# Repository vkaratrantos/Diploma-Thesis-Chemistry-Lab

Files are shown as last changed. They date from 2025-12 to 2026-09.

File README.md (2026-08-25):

# Automated Chemical Synthesis with a 7-DOF Robotic Arm

Diploma thesis — Electrical and Computer Engineering, University of Patras.
Division of Systems, Control and Robotics.

A robotic system that automates liquid-handling in a chemistry lab: it locates
test tubes visually, picks them up, carries them to a mixing vessel and pours,
keeping the tube upright throughout so nothing spills.

The system does not work from taught positions. Tube and vessel locations
come from ArUco markers detected at runtime, so the rack can be moved between
runs and the arm adapts.

---

## The problem

Three problems that a simple pick-and-place demo does not have:

1. The tube must stay upright.
2. Positions are not known in advance.
3. A 7-DOF arm is redundant.

---

## Hardware

| | |
| --- | --- |
| Arm | Elephant Robotics MyArm 300 Pi (7 DOF) |
| Gripper | Custom, Thorgripper |
| Camera | Creative Livecam HD |
| Markers | ArUco, 30 mm |
| Compute | Raspberry Pi on the arm + external PC for planning |

---

## How it works

```
camera ──► ArUco detection ──► TF frames (marker_1 … marker_6)
                                     │
                                     ▼
                       planning scene (tubes + mixing vessel)
                                     │
                                     ▼
                           MoveIt 2 ──► trajectory
                                     │
                                     ▼
                                MyArm 300 Pi
```

**Vision.** ArUco markers on the rack and the mixing vessel are detected and
published as TF frames.
Camera-to-arm calibration in aruco/calibrate_camera.py .

**Planning.** Approaches are planned backwards: IK solution found at the
grasp pose first, and the standoff above it is seeded from that solution, so
both ends share an IK branch. Each candidate standoff is then verified by
dry-running the actual descent from it before the arm commits to moving there.

**Keeping the tube upright.** Rather than asking OMPL to respect an orientation
constraint in the full 7-DOF space, transits search the 5-DOF manifold on which
the constraint is already satisfied — joints 1–4 plus the roll about the
vertical, with the wrist recovered in closed form.

---

## Repository layout

| Path | What it is |
| --- | --- |
| [`aruco/aruco_anchor.py`](aruco) | Marker detection, TF publishing |
| [`aruco/calibrate_camera.py`](camera_calibration) | Intrinsics and camera-to-arm calibration |
| [`robot_initialisation/`](MyArm%20300%20Pi) | Arm driver and hardware bridge |
| [`robot_initialisation/`](robot_initialisation) | Startup and homing |
| [`launch/`](launch) | Launch files — fake robot, Gazebo, real arm |
| [`config/`](config) | Kinematics, joint limits, OMPL settings |
| [`GUI/`](GUI) | Tkinter operator interface |
| [`3d_prints/`](3d_prints) | Custom bases and flange (STL files) |
| `simple_move.cpp` | Motion node |

---

## Running

Built and tested on **Ubuntu 22.04 / ROS 2 Humble**, with MoveIt 2 and
MoveIt Task Constructor built from source.

Three modes: fake robot (no hardware), Gazebo, and the real
arm.

### Commands

The GUI publishes on `/gui_commands`
| Command | Action |
| --- | --- |
| `TASK <1-5>` | Full pipeline for each tube |
| `m<0-6>` | Manual move to a marker |
| `o` / `c` | Open / close gripper |
| `p` | Pour |
| `h` | Return home |

## Related

The final packaged ROS 2 workspace is in
[**thesis-repo**](https://github.com/vkaratrantos/thesis-repo)

## Status

Thesis defence scheduled for September 2026. The system runs on the physical
arm; known limitations are documented in the workspace README.

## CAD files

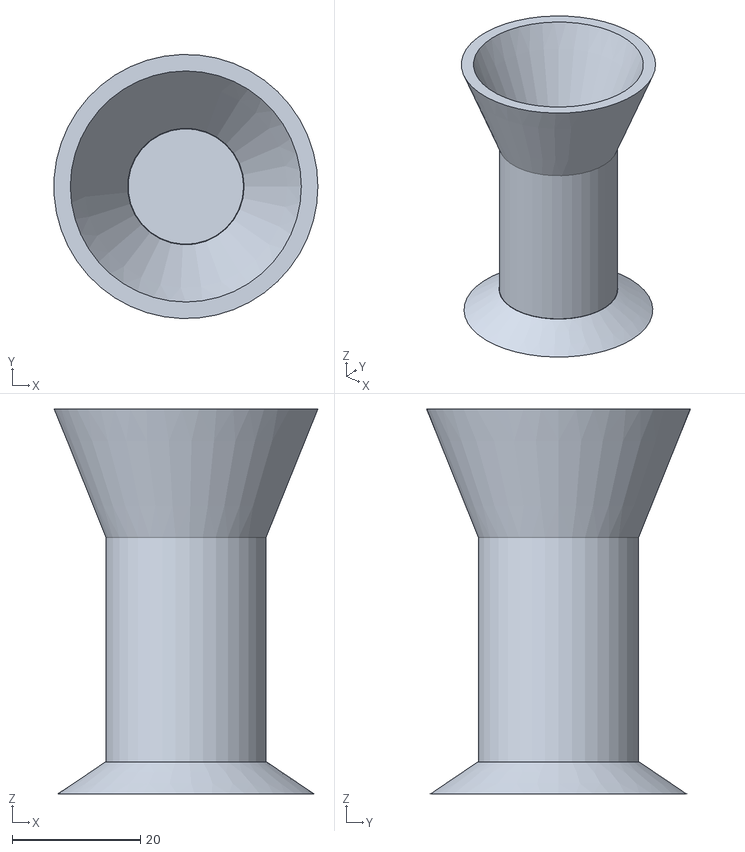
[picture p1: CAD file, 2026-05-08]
3d_prints/bracket_cone.stl
41.1 x 41.1 x 60.0

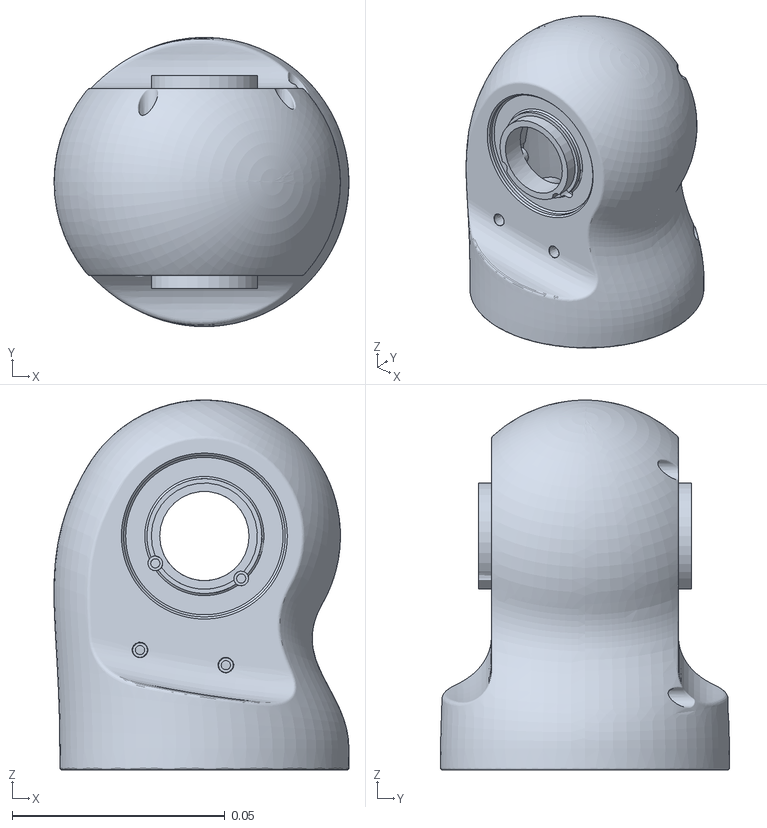
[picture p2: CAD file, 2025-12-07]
MyArm 300 Pi/URDF/j3.stl
0.0694 x 0.068 x 0.087

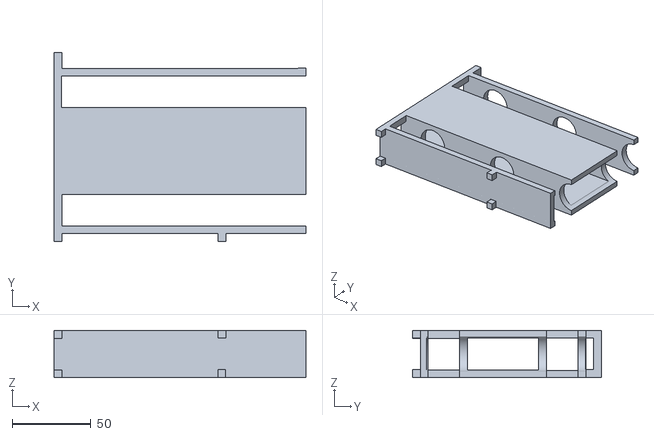
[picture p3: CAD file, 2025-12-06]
3d_prints/rack.stl
160.0 x 120.0 x 30.0

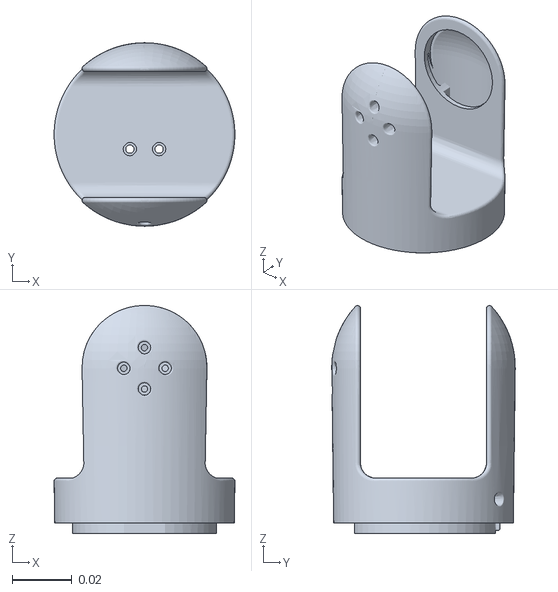
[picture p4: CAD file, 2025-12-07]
MyArm 300 Pi/URDF/j5.stl
0.0603 x 0.0613 x 0.0761

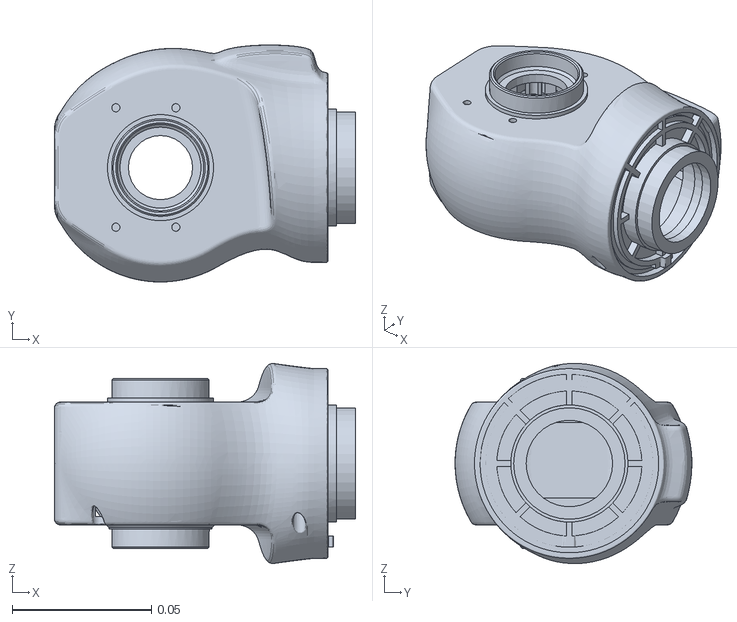
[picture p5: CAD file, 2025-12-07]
MyArm 300 Pi/URDF/j2.stl
0.108 x 0.0849 x 0.0718

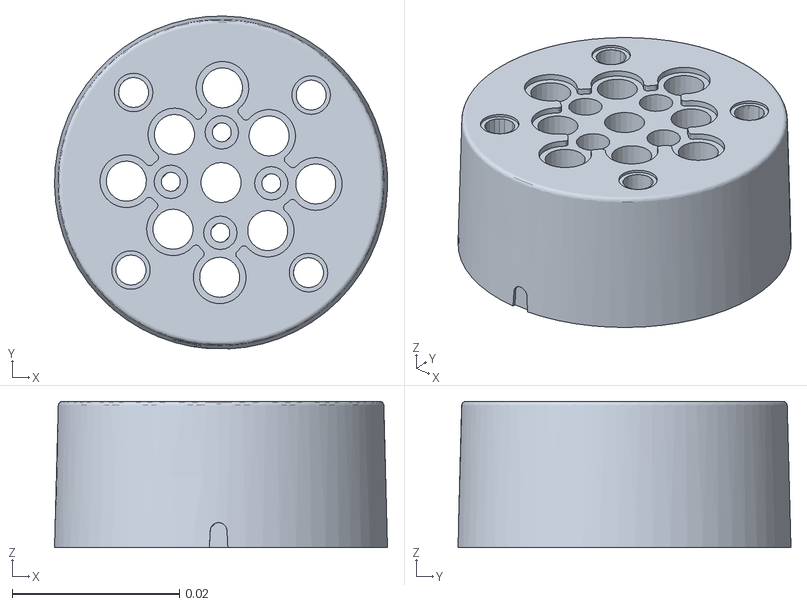
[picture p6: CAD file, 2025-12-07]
MyArm 300 Pi/URDF/j7.stl
0.0398 x 0.0398 x 0.0175

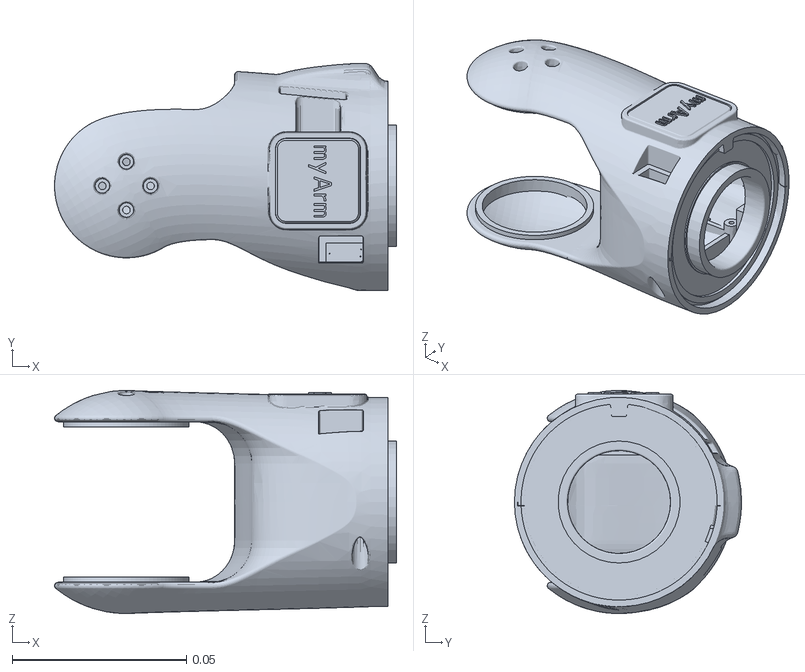
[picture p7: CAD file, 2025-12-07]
MyArm 300 Pi/URDF/j4.stl
0.098 x 0.0651 x 0.064

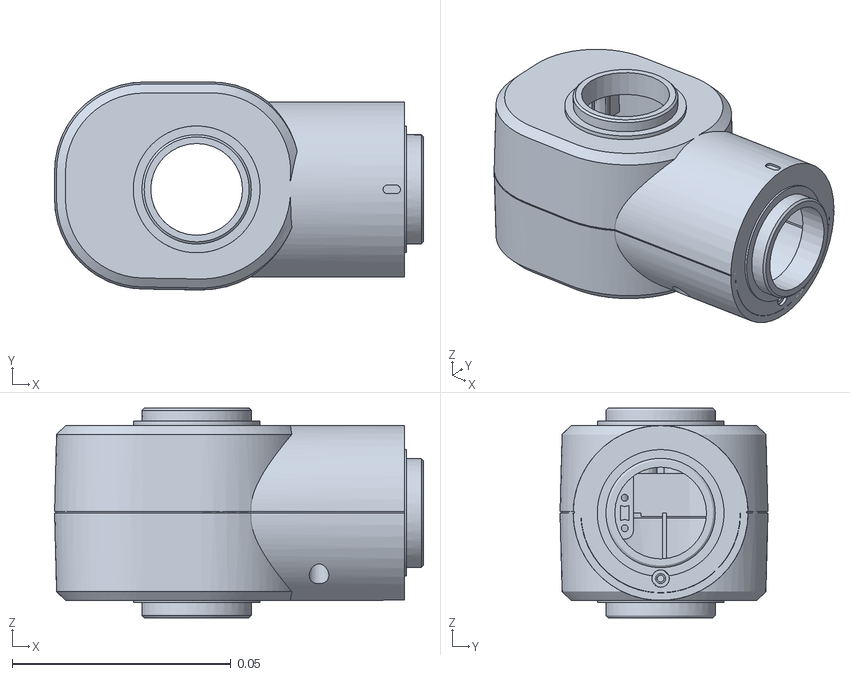
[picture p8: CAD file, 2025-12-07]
MyArm 300 Pi/URDF/j6.stl
0.0844 x 0.0476 x 0.048

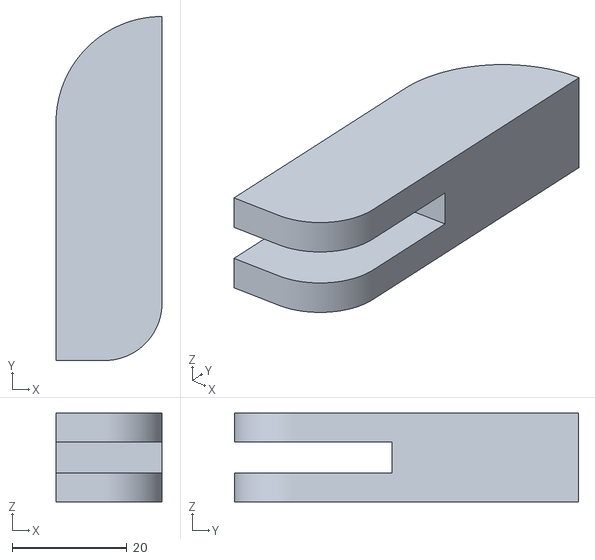
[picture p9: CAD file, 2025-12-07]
MyArm 300 Pi/URDF/GripperFinger.stl
18.5 x 60.0 x 15.5

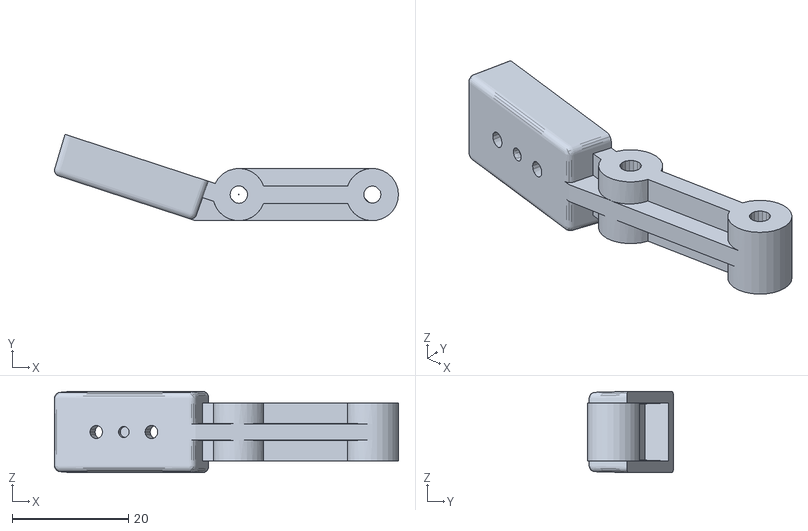
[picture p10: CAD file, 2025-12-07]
MyArm 300 Pi/URDF/gripper_left1.stl
59.3 x 14.9 x 14.0

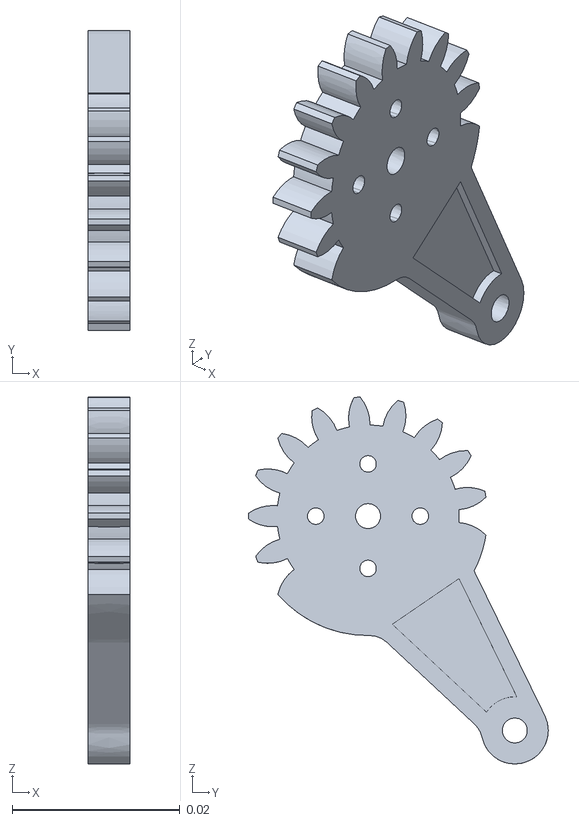
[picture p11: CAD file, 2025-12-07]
MyArm 300 Pi/URDF/gripper_right3.stl
0.005 x 0.0358 x 0.0438

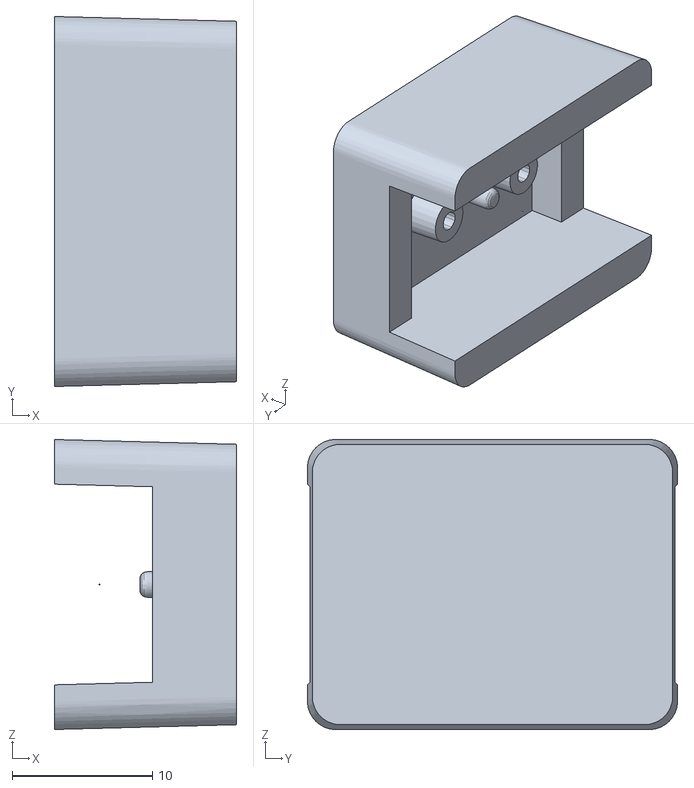
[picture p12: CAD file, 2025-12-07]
MyArm 300 Pi/URDF/gripper_right1.stl
13.0 x 26.4 x 20.7

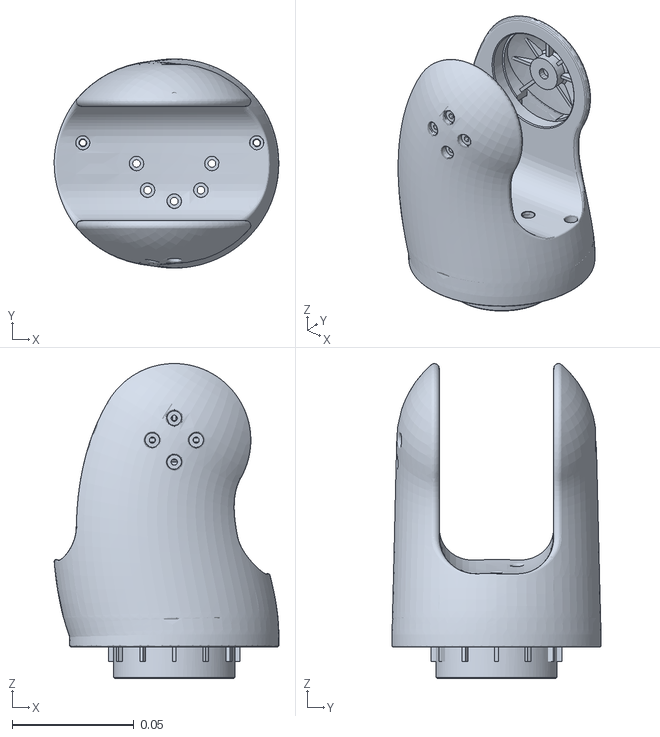
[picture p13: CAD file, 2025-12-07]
MyArm 300 Pi/URDF/j1.stl
0.0924 x 0.086 x 0.13

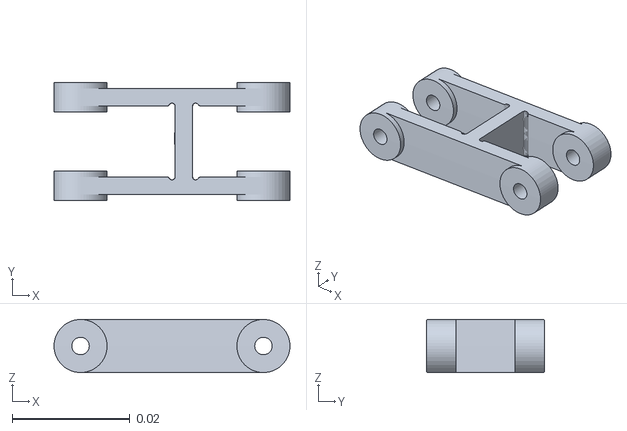
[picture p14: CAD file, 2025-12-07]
MyArm 300 Pi/URDF/gripper_left2.stl
0.04 x 0.02 x 0.009

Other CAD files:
MyArm 300 Pi/URDF/gripper_left3.stl
MyArm 300 Pi/URDF/gripper_right2.stl
MyArm 300 Pi/URDF/GripperArmGear.stl
MyArm 300 Pi/URDF/GripperBase.stl
MyArm 300 Pi/URDF/GripperArm.stl
MyArm 300 Pi/URDF/base.stl
MyArm 300 Pi/URDF/end_effector.stl
MyArm 300 Pi/URDF/flange.stl
MyArm 300 Pi/URDF/gripper_base.stl

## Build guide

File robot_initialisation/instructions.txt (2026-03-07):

MyArm 300 Pi - Direct LAN Control (Bypass Mode)

The file ros_lan_driver.py and the following procedure is used to connect the Elephant Robotics MyArm 300 Pi with a PC running ROS2 Humble.

The main goal is to control the arm "bypassing" the Raspberry Pi's internal ROS. The PC runs ROS2 and the Raspberry Pi acts as a simple bridge/server over a LAN cable.

ros_lan_driver.py: Runs on the PC and acts as the hardware driver.

Network Setup 

1. Connect the PC and the Robotic Arm directly using a LAN Cable.
2. Set the PC's wired IPv4 address to : 192.168.123.10
3. Set the Pi's wired IPv4 address to : 192.168.123.20

(Make sure to test the connection between the Pi and the PC using the command "ping" before the next steps)

Usage Instructions 

1. Raspberry Pi (Bridge)

SSH into the Raspberry Pi (or use a monitor and a keyboard) and run these commands to open the ports :

# Start the daemon for Gripper control (Port 8888)
$ sudo pigpiod

# Forward the Serial Port to the Network (Port 8889)
$ socat TCP-LISTEN:8889,fork,reuseaddr FILE:/dev/ttyAMA0,b115200,raw,echo=0

2. PC (Terminal 1 - Virtual Connection)

Create the virtual serial port that links with the Pi :

$ socat pty,link=/tmp/virtual_robot,raw tcp:192.168.123.20:8889

Keep the terimal open

3. PC (Terminal 2 - The Driver)

Navigate to the folder containing ros_lan_driver.py and run the file.

Example:

$ cd ~/my_robot
$ python3 ros_lan_driver.py --ros-args -r joint_states:=/hardware_joints

Wait until you see the message that confirms the connection

4. PC (Terminal 3 - Driver 2)

$ cd ~/my_robot
$ python3 moveit_bridge_5.py

5. PC (Terminal 4 - The Controller)

With the driver running, you can finally control the robot.

We will choose to control it through moveit and we will visualise the robot.

Example :

$ ros2 launch robot_config real.launch.py

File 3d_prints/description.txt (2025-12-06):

The "flange.stl" file describes the flange that connects the joint7 and the Thorgripper.
The "rack.stl" file describes the rack where the test tubes are put, but it is cut in the middle in order to be sliced.

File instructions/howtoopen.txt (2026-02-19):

Ιn the PC:

Terminal 1:
source ~/.bashrc
socat

Terminal 2:
source ~/.bashrc
driver

Terminal 3:
source ~/.bashrc
bridge

Terminal 4:
source ~/.bashrc
start

Terminal 5:
source ~/.bashrc
cd aruco
python3 aruco_anchor.py

Terminal 6:
cd elephant_robots_ws
colcon build --packages-select my_robot_control
source install/setup.bash
ros2 run my_robot_control move_to_marker

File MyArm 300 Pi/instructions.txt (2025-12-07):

If you want to use the modified workspace for the MyArm 300 Pi robot with the Thorgripper, you have to follow these instructions :

1. Install and build the official Elephant Robotics workspace (https://github.com/elephantrobotics/mycobot_ros2). Make sure to select the branch correctly, according to your version (for me it's Humble).
2. Replace the URDF folder in 'src/mycobot_ros2/mycobot_description/urdf/myarm_300_pi' with the URDF folder here.
3. Correct the URDF filename and path in the launch files (if you have changed it).
4. Build your workspace again.
5. Launch one of the launch files.

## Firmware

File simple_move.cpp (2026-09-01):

// ============================================================================
//  LIQUID HANDLING 7-DOF ROBOTIC ARM
//  MoveIt 2 + MoveIt Task Constructor
//
//  Commands (published as std_msgs/String on /gui_commands):
//    TASK <1-5>   full MTC pick-and-carry pipeline for that tube
//    m<0-6>       manual hybrid move to a marker (OMPL transit + Cartesian descent)
//    <x> <y> <z>  manual hybrid move to raw coordinates
//    o            open gripper (detaches held tube)
//    c            close gripper (attaches tube at current marker)
//    p            pour
//    h            return to home pose
//    q            quit
// ============================================================================

// ---- BUILD NOTE ------------------------------------------------------------
// Uncomment the following line if you are building against MoveIt 2 Jazzy or
// newer, where computeCartesianPath() takes MaxEEFStep / JumpThreshold structs
// instead of plain doubles.
//
// #define MOVEIT_JAZZY_OR_NEWER 1
// ----------------------------------------------------------------------------

#include <atomic>
#include <chrono>
#include <cmath>
#include <iostream>
#include <limits>
#include <memory>
#include <mutex>
#include <queue>
#include <sstream>
#include <string>
#include <thread>
#include <vector>
#include <algorithm>

#include <rclcpp/rclcpp.hpp>
#include <std_msgs/msg/string.hpp>

#include <geometry_msgs/msg/pose.hpp>
#include <geometry_msgs/msg/pose_stamped.hpp>
#include <geometry_msgs/msg/transform_stamped.hpp>
#include <geometry_msgs/msg/vector3_stamped.hpp>
#include <moveit_msgs/msg/collision_object.hpp>
#include <moveit_msgs/msg/constraints.hpp>
#include <moveit_msgs/msg/orientation_constraint.hpp>
#include <moveit_msgs/msg/robot_trajectory.hpp>
#include <shape_msgs/msg/solid_primitive.hpp>

#include "my_robot_control/manifold_planner.hpp"
#include "my_robot_control/path_lifter.hpp"

#include <moveit/robot_trajectory/robot_trajectory.h>
#include <moveit/trajectory_processing/time_optimal_trajectory_generation.h>

#include <tf2/LinearMath/Quaternion.h>
#include <tf2_geometry_msgs/tf2_geometry_msgs.hpp>   // tf2::toMsg
#include <tf2_ros/buffer.h>
#include <tf2_ros/transform_listener.h>

#include <Eigen/Geometry>

#include <moveit/move_group_interface/move_group_interface.h>
#include <moveit/planning_scene_interface/planning_scene_interface.h>
#include <moveit/planning_scene_monitor/planning_scene_monitor.h>
#include <moveit/collision_detection/collision_matrix.h>
#include <moveit_msgs/msg/planning_scene.hpp>
#include <moveit/robot_model/joint_model_group.h>
#include <moveit/robot_state/robot_state.h>
#include <moveit/robot_trajectory/robot_trajectory.h>
#include <moveit/trajectory_processing/time_optimal_trajectory_generation.h>

// ---- MoveIt Task Constructor ----------------------------------------------
#include <moveit/task_constructor/task.h>
#include <moveit/task_constructor/solvers/cartesian_path.h>
#include <moveit/task_constructor/solvers/joint_interpolation.h>
#include <moveit/task_constructor/solvers/pipeline_planner.h>
#include <moveit/task_constructor/stages/current_state.h>
#include <moveit/task_constructor/stages/modify_planning_scene.h>
#include <moveit/task_constructor/stages/move_relative.h>
#include <moveit/task_constructor/stages/move_to.h>

namespace mtc = moveit::task_constructor;
using MGI = moveit::planning_interface::MoveGroupInterface;

// ============================================================================
//  CONSTANTS
//  Every magic number lives here. In the original file the tube height and the
//  mixer radius were defined differently in setupCollisionObjects() and in the
//  dynamic updater, so the scene silently changed shape 500 ms after startup.
// ============================================================================

// ---- Speed scaling ---------------------------------------------------------
// These only started meaning anything once fake_robot.py was made to honour
// time_from_start; before that every trajectory was replayed at a flat 20 ms
// per waypoint and the scaling was inert.
//
// Nothing here is velocity-limited in practice -- with max_velocity 3.0 and
// max_acceleration 3.0 from joint_limits.yaml, the moves are entirely
// acceleration-limited, so ACC_SCALE is the knob that changes how long a move
// takes. VEL_SCALE effectively does nothing at these values.
//
// The 2:1 ratio between transit and liquid is deliberate and worth keeping:
// carrying a full tube should visibly be the gentler motion.
static constexpr double VEL_SCALE_TRANSIT = 0.30;
static constexpr double ACC_SCALE_TRANSIT = 0.30;
static constexpr double VEL_SCALE_LIQUID  = 0.15;   // slower when carrying
static constexpr double ACC_SCALE_LIQUID  = 0.15;

// Gripper closing/opening speed. MoveGroupInterface defaults to 0.1 and nothing
// ever overrode it, so these halve that -- about half the previous speed.
// Adjust both together; the travel is short enough that acceleration dominates.
static constexpr double GRIPPER_VEL_SCALE = 0.05;
static constexpr double GRIPPER_ACC_SCALE = 0.05;

// ---- Table -----------------------------------------------------------------
static constexpr double TABLE_SIZE_XY   = 1.5;
static constexpr double TABLE_THICKNESS = 0.04;
static constexpr double TABLE_CENTER_Z  = -0.03;    // -> top surface at z = -0.01

// ---- Test tubes ------------------------------------------------------------
static constexpr double TUBE_HEIGHT = 0.1;
static constexpr double TUBE_RADIUS = 0.008;
// NOTE: geometrically this should be table_top + height/2 = -0.01 + 0.065 = 0.055.
// Your original code used 0.07 at init and 0.08 in the updater. 0.08 is kept
// here to preserve the behaviour you tuned against, but verify it in RViz --
// if it is wrong, the tube collision cylinder floats 2.5 cm above the table
// and the gripper can clip the real tube without the planner noticing.
static constexpr double TUBE_CENTER_Z = 0.06;

// marker -> tube body, in y. Together with GRASP_Y_OFFSET below this implies a
// 135 mm gap, which is correct: that gap is the distance from the flange (where
// the TCP frame is) out to the fingertips. See TUBE_TCP_Y_OFFSET.
static constexpr double TUBE_Y_OFFSET = 0.02;

// ---- Mixer -----------------------------------------------------------------
static constexpr double MIXER_HEIGHT   = 0.1;
static constexpr double MIXER_RADIUS   = 0.04;      // updater used 0.05; unified
static constexpr double MIXER_CENTER_Z = 0.05;      // updater used 0.07; unified
static constexpr double MIXER_Y_OFFSET = 0.07;   // mixer body = marker_6 + this, in y

// ---- Grasp geometry --------------------------------------------------------
// marker -> TCP, in y. This is the number the arm has actually been driven with.
static constexpr double GRASP_Y_OFFSET = 0.155;
static constexpr double GRASP_Z        = 0.11;      // TCP height at the tube
static constexpr double POUR_Z         = 0.20;      // TCP height above the mixer
static constexpr double APPROACH_DIST  = 0.1;      // vertical descent to grasp
static constexpr double LIFT_DIST      = 0.12;      // vertical retreat after grasp
static constexpr double STANDOFF_TUBE  = 0.10;

// How much rotation about the tool axis the interpolator may invent when a
// strict straight line fails. A test tube is a cylinder, so spin about its long
// axis does not change the grasp -- that freedom is yours to spend.
// Set to 0.0 if your gripper fingers are asymmetric or a cable would wrap.
// Rotation the interpolator may invent about the tool axis when a strict
// straight line fails.
//
// DISABLED (0.0), and it should stay that way unless you change the gripper.
// The tube axis is the TCP frame's X, but the grasp point is 135 mm OFF that
// axis, so rotating about it does not spin the tube in place -- it swings the
// tube around a 135 mm radius, up to 270 mm of lateral travel. During a descent
// into the rack that would sweep the fingers right off the tube, or into its
// neighbours. Free-axis relaxation is only safe when the grasp point lies ON
// the axis of symmetry, which here it does not.
//
// (The orientation CONSTRAINT still frees X, and that is correct: rotating about
// a vertical axis keeps the tube upright, so nothing spills. Constraint and
// interpolator are asking different questions.)
static constexpr double TOOL_AXIS_FREEDOM = 0.0;

// How close to a joint stop a standoff configuration may sit, in radians.
//
// Not a tuning knob so much as a feasibility floor. A configuration in bounds
// but hard against a limit has no room to descend: measured on the real task,
// the arm reached the standoff with joint5 at 2.962 against a 2.967 limit --
// 0.005 rad of headroom -- and the descent stalled at 11% because continuing
// required flipping joint5 by 2.80 rad to the mirror wrist branch. The working
// configuration at the same pose sat at joint5 = 0.065, with 2.90 rad spare.
//
// The measured populations are far apart: every configuration that stalled a
// descent had headroom below 0.01 rad (0.005, 7e-05, 5e-06, 1e-05), while every
// working one measured 0.18 or more. 0.05 sits in the empty gap between them,
// rejecting every observed failure by a factor of five while leaving the
// marginal cases to the dry run -- which is the authoritative test and costs
// only ~250 ms.
//
// This started at 0.15 and that was too aggressive: it threw away candidates
// with 0.128-0.131 rad of headroom without ever testing them, which pushed the
// search through all six generators (3.8 s of IK) and down to a lower standoff
// height for no reason.
static constexpr double LIMIT_HEADROOM_MIN = 0.05;

// ---- Upright transits with an empty gripper --------------------------------
// ON by default: the tool is now kept upright whether or not a tube is held.
// There is nothing to spill with an empty gripper, but an unconstrained transit
// tilts the tool up to 32.5 degrees and arrives in whatever configuration OMPL
// liked, which is what the descent then has to live with.
//
// Kept as a runtime toggle ('u' on /gui_commands) rather than deleted, because
// it is the A/B control for the descent-stall bug this fixes: flipping it back
// restores the legacy joint-target transit without a rebuild.
static std::atomic<bool> g_upright_when_empty{true};

// How far the tube may tip from vertical during a carrying move, in radians.
// 0.10 rad is about 6 degrees. Tighter is safer for the liquid but much harder
// for OMPL to plan -- see the note on enforce_constrained_state_space below.
static constexpr double TILT_TOLERANCE = 0.3;
static constexpr double STANDOFF_MIXER = 0.12;

// ---- Misc ------------------------------------------------------------------
// ---- Where the carried tube sits relative to the TCP ----------------------
// getEndEffectorLink() returns the FLANGE, not the fingertips. The gripper
// reaches ~135 mm beyond it, so a tube held between the fingers sits that far
// from the TCP frame origin. Setting these to zero puts the tube at the wrist,
// which is exactly what it looks like in RViz when you get it wrong.
//
// This is also why TUBE_Y_OFFSET (0.02) and GRASP_Y_OFFSET (0.155) differ:
//   marker -> tube      = 0.020
//   marker -> flange    = 0.155
//   flange -> fingertips= 0.135   <- the gripper's own length
// so the fingers land at 0.155 - 0.135 = 0.020 = the tube. Consistent, not
// contradictory. Verify by grabbing a tube and looking in RViz: the cylinder
// must appear between the fingers.
static constexpr double TUBE_TCP_Y_OFFSET = -0.135;  // -0.135
static constexpr double TUBE_TCP_Z_OFFSET = -0.01;            // -0.030

static constexpr double MIXER_TOP_Z = MIXER_CENTER_Z + MIXER_HEIGHT / 2.0;   // 0.100
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

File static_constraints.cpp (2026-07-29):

// LIQUID HANDLING 7-DOF ROBOTIC ARM -- FINAL VERSION

#include <memory>
#include <thread>
#include <iostream>
#include <string>
#include <sstream>
#include <cmath>
#include <vector>
#include <chrono>
#include <queue> 
#include <mutex>
#include <atomic>
#include <moveit/trajectory_processing/trajectory_tools.h>
#include <moveit/robot_trajectory/robot_trajectory.h>
#include <moveit/trajectory_processing/time_optimal_trajectory_generation.h>
#include <rclcpp/rclcpp.hpp>
#include <std_msgs/msg/string.hpp> 
#include <moveit/move_group_interface/move_group_interface.h>
#include <moveit_msgs/msg/robot_trajectory.hpp>
#include <moveit_msgs/msg/constraints.hpp>
#include <moveit_msgs/msg/orientation_constraint.hpp>
#include <geometry_msgs/msg/pose.hpp>
#include <tf2/LinearMath/Quaternion.h>
#include <moveit/planning_scene_interface/planning_scene_interface.h>
#include <moveit_msgs/msg/collision_object.hpp>
#include <shape_msgs/msg/solid_primitive.hpp>
#include <tf2_ros/buffer.h>
#include <tf2_ros/transform_listener.h>
#include <geometry_msgs/msg/transform_stamped.hpp>

// CONSTANTS

static constexpr double VEL_SCALE_TRANSIT  = 0.3; 
static constexpr double VEL_SCALE_LIQUID   = 0.3; 
static constexpr double ACC_SCALE_TRANSIT  = 0.1;
static constexpr double ACC_SCALE_LIQUID   = 0.1;

// MOTION VARIABLES

static constexpr int    STATE_SETTLE_MS    = 500;

// QUEUE

std::queue<std::string> command_queue;
std::mutex queue_mutex;

// COLLISION OBJECTS

// Modified to accept tf_buffer so it can spawn tubes relative to live markers

void setupCollisionObjects(const std::string& frame_id, tf2_ros::Buffer& tf_buffer) {

    moveit::planning_interface::PlanningSceneInterface planning_scene_interface;
    std::vector<moveit_msgs::msg::CollisionObject> collision_objects;

    // TABLE SURFACE COLLISION OBJECT
    
    moveit_msgs::msg::CollisionObject table;
    table.id = "table_base";
    table.header.frame_id = frame_id;
    table.primitives.resize(1);
    table.primitives[0].type = shape_msgs::msg::SolidPrimitive::BOX;
    table.primitives[0].dimensions = {1.5, 1.5, 0.04}; 
    table.primitive_poses.resize(1);
    table.primitive_poses[0].position.x = 0.0;
    table.primitive_poses[0].position.y = 0.0;
    table.primitive_poses[0].position.z = -0.03; 
    table.primitive_poses[0].orientation.w = 1.0;
    table.operation = table.ADD;
    collision_objects.push_back(table);

    // 1ST BOX OBJECT

    moveit_msgs::msg::CollisionObject wall;
    wall.id = "obstacle_box";
    wall.header.frame_id = frame_id;
    wall.primitives.resize(1);
    wall.primitives[0].type = shape_msgs::msg::SolidPrimitive::BOX;
    wall.primitives[0].dimensions = { 0.7, 0.2, 0.05 };
    wall.primitive_poses.resize(1);
    wall.primitive_poses[0].position.x = 0.0;
    wall.primitive_poses[0].position.y = 0.18;
    wall.primitive_poses[0].position.z = 0.02;   
    wall.primitive_poses[0].orientation.w = 1.0;
    wall.operation = wall.ADD;
    collision_objects.push_back(wall);

    // 2ND BOX OBJECT
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

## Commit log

2025-12-06 Update 3D print descriptions in description.txt
    Added descriptions for 'rack.stl' and 'flange.stl'.
2025-12-07 Add URDF definition for MyArm 300 Pi
    This URDF file defines a robotic arm named 'firefighter' with multiple links and joints, including a gripper mechanism.
2025-12-07 Add URDF for MyArm 300 Pi robot
    This commit adds a URDF file for the MyArm 300 Pi robot, defining its structure, links, joints, and materials.
2026-03-06 Add ArucoAnchor class for dynamic camera system
2026-03-10 Add Y-offset for specific markers and include headers
    Added a 6cm Y-offset for markers 1 to 5 to adjust target position. Included necessary headers for functionality.
2026-05-15 Adjust scales, add obstacle, and reduce planning time
    Updated velocity and acceleration scales for transit and liquid. Added a second obstacle box to the collision setup and reduced planning time for various planning stages.
2026-05-15 Refactor MoveItBridge for multi-threading support
2026-05-17 Implement safety locks and debouncing for commands
    Added safety locks and debouncers to prevent double-firing of commands in the GUI. Updated command sending logic to handle manual commands with a debouncer and unified thread logic for batch processi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
2026-05-19 Refactor liquid handler with command queue and mutex
    Added command queue and mutex for thread safety. Updated drop and lift methods to improve functionality. Removed unused functions and adjusted Z-axis movement parameters.
2026-05-21 Change anchor ID and video capture device
